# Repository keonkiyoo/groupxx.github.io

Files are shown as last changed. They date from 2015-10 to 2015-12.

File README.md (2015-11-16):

# groupxx.github.io

Team Smart Cane - T06
Group Members: Shadman Shamin, Keon Yoo, Nate Pham, Dusan Micic

Project Description: The development and implementation of a smart cane that read surrounding environment and measures distance between the user and obstacles. The cane is for everybody who uses a cane and geared towards elderly population to help them navigate the streets and pedestrians safely. Based on the threshold safe distance the cane sends a haptic feedback to user to notify/alert the user of nearby obstacles so that they can avoid the obstacles safely.

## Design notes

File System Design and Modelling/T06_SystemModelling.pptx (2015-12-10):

## T06 - Smart Cane System Modelling

Members: Dusan Micic, Shadman Samin, Nathan Pham, Keon Yoo

Document ID: T06_Model_V1
Version : 1.1
Date : 12/9/2015
Location : Git Wiki Page (https://github.com/keonkiyoo/groupxx.github.io/wiki)

## Level - 0 Diagram

3 different Ultrasonic Sensor Inputs

Smart Cane

Power, 9V DC

Haptic Motor Output

Module | Smart Cane
Inputs | The system has three pulse width inputs coming in from 3 Ultrasonic Sensors. Each containing an 8 cycle burst pulses that gives us distance information based on the width of the pulse. Second, we have the 9V DC Power that is connected to the 9V battery that powers the whole system.
Outputs | Digital Output to Haptic Motor for operation
Functionality | Measure the distance between the user and nearby objects. And notifies the user if the object is too close.

## Level 1: Smart Cane

Ultrasonic-1

Ultrasonic-2

Ultrasonic-3

Digital Input/Output

Digital Input/Output

Digital Input/Output

Application Software

SPI Interface Program & Debug

Digital Input/Output

Microprocessor

Digital Output

Haptic Motors

Regulator: 5V

Regulator: 3.3V

9V Battery

## Level - 0: 5V Regulator

Regulator: 5V

Power, 9V DC

5 V (DC)

Module | Regulator: 5V
Inputs | Battery connection with a +9V DC Battery
Outputs | +5V DC Output, Maximum Current: 1A
Functionality | Output a constant 5V DC output from a 9 V

## Level - 0: 3.3V Regulator

Regulator: 3.3V

Power, 9V DC

3.3V (Analog DC)

Module | Regulator: 3.3V
Inputs | Battery connection with a +9V DC Battery
Outputs | +3.3V DC Output, Maximum Current: 1A
Functionality | Output a constant 3.3V output from a 9V

## Level - 0: Ultrasonic Sensor

Ultrasonic Sensor

5V DC, Power

Digital Input/Output

Module | Ultrasonic Sensor
Inputs | 5V DC Input for the Ultrasonic Sensor(From 5V Voltage Regulator)
I/O (Input/Output) Pin | The Microprocessors sends a digital trigger pulse (5V) to the ultrasonic sensor to activate it. The sensor sends back an echo signal by an 8 cycle burst pulse (~5V) on the same pin to the microprocessor. The width of the digital pulse to the microprocessor indicates the obstruction distance. The wider the signal the further the object.
Functionality | Every 100 ms the sensor receive a 10 us trigger to activate it and send back a digital pulse to the microcontroller which contains distance information.

## Level - 0: Microprocessor

Digital Input/Output

Microprocessor

Digital Output (Motors)

5V DC, Power

Module | Microprocessor
Inputs | 5V DC Input for Power (From 5V Regulator) Input 8 burst cycle from the echo of ultrasonic sensor to detect distance.
Outputs | Send output high (~5V) to bias transistor allowing current flow to power motor on when within obstruction distance Output 10us pulse high (~5V) to trigger the Ultrasonic sensors
Functionality | When the microcontroller gets an input from the Ultrasonic sensors it looks at the width of the return pulse to find the distance between the user the object in front. If the distance is less than the safe distance the Digital pins on the outputs go High to notify the user.

## Level - 0: Haptic Motor

Digital Input

3.3V DC, Power

Haptic Motor

Motor Vibration Output

Module | Haptic Motor
Inputs | 3.3V DC Input (from 3.3V Voltage Regulator) Digital Input Connection from Microprocessor (output high ~5 volts)
Outputs | Motor Vibration Output
Functionality | If the Sensors detect an object too close to the user the Microprocessor sends a high bit through one of the digital ports on the microprocessor to turn on the Haptic motors (4.5 – 3.0 Volt required power to operate) to warn the user of an obstruction.

## Smart Cane Flowchart Representation

No

Start

Object Detection

Calculate the distance between Object and Cane

Distance < 30 cm

Yes

Turn on the LED and Haptic Motors to Alert the User

No

Distance < 30 cm

Yes

## State Machine View

Within Motor distance

object detected

No object detected

User Feedback and Operate Motor

Verify Distance

Object Detection

Re-verify distance

Not within motor distance

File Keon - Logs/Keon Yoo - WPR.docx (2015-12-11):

10/11/15 – 10/17/15

Accomplished: Set up the Github page and downloaded desktop GUI for Github. We also narrowed down the design specifications.

10/18/15 – 10/24/15

Accomplished: Met with the team to test Arduino code and the ultrasonic sensors to make sure it was sufficient for the project. We found that the ultrasonic sensor is accurate upwards of 2.5m.

10/25/15 – 10/31/15

Accomplished: Worked on learning how to use the EagleCAD to do the schemaitcs. Worked with Shadman on completing the schematics for the board design.

11/1/2015 – 11/7/2015

Accomplished: Started working on the programming microcontroller. We were having trouble getting the Arduino to program the Atemga 328p on the bread board. One of the students told us to use the AVR dragon to program it and we were able to program the microcontroller.

11/8/2015 – 11/14/2015

Accomplished: Nate and I completed set of code which lighted LED on and off to ensure that microcontroller was working. We set up a sensor for the circuit with a clock pulse which we generated through a code, periodi 100us pulse.

11/15/2015 – 11/21/2015

Accomplished: I found a code online that was used for operating the sensor with the idea of the rising edge pulse and falling edge. However it was beyond our scope of understanding for coding the sensor. We changed the various value within the code that we knew would not result in significant difference in the detection of objects.

11/22/2015 – 11/28/2015

Accomplished: This week we met up as a team to debug and construct our PCB we got from OSH Park. However there were some error on the PCB, it was not matching with the EagleCAD. It was a minor error so we decided it was okay and we ordered correct size parts. However, when we plugged the assembled board to the AVR dragon to program it, it gave us an error saying not enough voltage, so we walked through the circuit and decided to remove the reset LED to give more voltage to the Atmega328p. However, that still did not work. Later in the evening, Shadman told us that it was AVR dragon that was causing the problem and everything was working fine. I soldered the wires that will run through the cane and the board.

11/29/2015 – 12/5/2015

Accomplished: New parts arrived and populated rest of the board. We got together and put together the cane. Nate and I worked on routing the wires through the cane. We had to make some adjustments such as cutting out a hole on the PVC pipe cane to route the wires. Shadman used laser cutter to print out the acrylic case for the board.

12/6/15-12/10/15

Accomplished: We spent this week working on the debugging and optimizing the code. We also worked on the power point presentation and revisions on the HW.

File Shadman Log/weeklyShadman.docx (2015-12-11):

Week 1 | Look for team members, submit resume.
Week 2 | Team formed. Look for parts to be used in the project. Brainstorm project ideas from different project website. Submit Project Proposal.
Week 3 | Built a rough prototype using the sonar sensors. Wrote a small code to interface with the arduino. Meet up with team members to work on the Wiki page
Week 4 | Worked on the product design specification
Week 5 | Worked on the schematic and the design timeline
Week 6 | Accomplishment: The schematic and the board layout is done
Week 7 | Accomplishment: The final boards are waiting to be shipped in. All the parts are ordered
Week 8 | Accomplishment: Final boards are populated with new right order of packages in the LID lab, the boards are tested and can talk to the computer using ISP header. Problems: We discovered the ISP header orientation on the board is not consistent with ISP header on the AVR dragon. Therefore, we spent alot of time trying to debug it.
Week 9 | Accomplishment: Prototype built. PVC cane retrofitted with Three sonar sensors and Laser cut a board to house the board. The vibration motors and all the wires are hidden inside the sensors. Problems: At this stage our prototype is working with three sensors working together to notify the user using haptic feedback.
Week 10 | Accomplishment: Got the prototype working for the final demonstration. Changed the software code to reflect changes. Problems: The sensor does not calculate the distance accurately based on the functional verification testing. Therefore, we changed the code to reflect and react to some arbitrary distance value. The BJT was replaced to reflect a fast switching circuit using a NMOS transistor.

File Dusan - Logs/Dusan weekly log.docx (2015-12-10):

10/11/15 – 10/17/15

Accomplished: Set up the Github page learned how to use it. Got familiar with git bash and git command line in general.

10/18/15 – 10/24/15

Accomplished: Met with the team to test Arduino code and the ultrasonic sensors to make sure it was sufficient for the project. We found that the ultrasonic sensor is accurate upwards of 2.5m.

10/25/15 – 10/31/15

Accomplished: Learned how to use EagleCAD to make the board from the schematic. Designed the board and debugged various issues and DRC errors until it was error free.

11/1/2015 – 11/7/2015

Accomplished: Downloaded Atmel studio to help with programing the microcontroller. The group got together to do initial tests on the range sensors and we made sure the frequency of the resonator we were using was sufficient.

11/8/2015 – 11/14/2015

Accomplished: We ordered the necessary parts for the board and sent the board off to get manufactured.

11/15/2015 – 11/21/2015

Accomplished: We received the parts and were still waiting for the boards to be manufactured.

11/22/2015 – 11/28/2015

Accomplished: We received the PCB’s from the manufacturer and began to learn how to apply solder paste, place components and baked in the oven. Shadman and I got together and populated two boards initially. We discovered that some of the parts were of the wrong size and we ordered new ones to correct for this. Other than the resonator (which was to small for its pads), everything on the board worked fine.

11/29/15 – 12/5/15

Accomplished: The new parts arrived and the whole group got together and populated the other two boards. All components fit perfectly. We built the cane prototype using PVC pipe.

12/6/15 – 12/10/15

Accomplished: This week we spent most of the time debugging various problems with the prototype and fine tuning the code. Next we got to work on the presentation and the various documentation that needs to be turned in.

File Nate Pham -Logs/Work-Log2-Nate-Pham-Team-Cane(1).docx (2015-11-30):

11/1/2015 – 11/7/2015

Accomplished: This week no battery indicator circuit was implemented. At the start of this week, Keon and I started working to get the microcontroller to be programmed on the breadboard itself and we were getting used to the software to operate the arduino and program the microcontroller and how to program the microcontroller on the board with various connections. We spend much of the time figuring out how to program the microcontroller on the arduino after researching through various websites we were unable to find anything that was usable through the information. A fellow student helped us though. He let us know that we should be using the AVR dragon with Atmel studio to program the chip on the arduino. We went to program the chip and were able to get the chip removed from the circuit and place it on the breadboard to ensure the effectiveness of the programming which ended up working well.

11/8/2015 – 11/14/2015

Accomplished: The time spent this week was recreating the circuit of the Arduino Nano on the breadboard with an external oscillator and connections to set pins. I set up the replicated circuit on the breadboard and began testing for the functionality of the microcontroller. Keon and I completed a set of code which set an output of the chip to blink on and off for and LED to ensure that it was working correctly. It ended up working well but with less output voltage than expected. We messed around with different coding structures for running the microcontroller and found various codes online that we tested but were fairly incomplete for the complete circuitry. We set up a sensor for the circuit with a clock pulse which we generated through a code which was a periodic 100us pulse. The result of the sensor though was a constant distance detection. We realized how the sensor operates but measuring the rising edge of the sent back signal to the falling edge of the signal and that is how it signifies the distance of the obstruction or object. I started tweaking with some characteristics of the clock pulse but only further realized that a constant clock pulse will not work for the circuitry.

11/15/2015 – 11/21/2015

Accomplished: Keon found a code online that was used for operating the sensor with the idea of the rising edge pulse and falling edge in consideration and it was beyond our scope of understanding for coding the sensors. We changed various values within the coding which we know that we could change without much difference to the detection of objects but we made sure the sensors still worked when changing up the code.

I ended up testing the circuit. I found that the result was when I set the motor to vibrate within 5 centimeters that the sensor would detect within that range but going from ~10cm – 15cm that there would be some detection of some obstruction though the sensor shouldn’t consider such a distance since it is beyond its notifying parameter. This was a consistent issue. I tried changing the ranges of detection and even with various values it kept on a having a repetitive result. I decided to pass off the results to Shadman for he wanted to test some things with the circuit.

11/22/2015 – 11/28/2015

Accomplished: This week we met up as a team to work on the board debug and construction. The boards were received from the EPL lab and Shadman and Keon did some of the soldering of the basic circuitry. We realized that when the boards were sent in that it was actually an incorrect schematic rather than the newest and updated one. Shadman was reviewing why an LED was as bright as the other LEDs and as a group we confirmed that it was okay.

We went over why there was only ~1.7 volts dropped from the reset switch to ground. It wasn’t a big deal until we got help from another student which he said that there needs to be a more significant voltage felt on the reset connection to program the chip. I noticed that the path to ground after the pull up resistor had a 220 ohm resistor and a LED on another path to ground which was in parallel with the reset switch. It became obvious that the path wasn’t dropping a significant voltage. The group suggested putting on a 10k ohm resistor before the LED to ensure that the voltage drop was >2.5 volts since the LED will drop .7 volts and the two 10k resistors are in a voltage divider configuration. The remeasured voltage to group was ~3 volts which was good for programming the chip.

Shadman and I then set up the chip to be programmed through the ISP pins to the AVR dragon and we weren’t able to get it to detect the voltage of the chip meaning that there was an error somewhere in the configuration. Shadman realized that one of the pins was incorrectly connected to the AVR dragon since each pin was wired with individual wires with male connectors separately in the AVR dragon input. Once that was adjusted, we received another error. I suggested to change the AVR dragon since I knew the AVR dragon and Atmel studio were fairly inconsistent in their operation. Once the AVR dragon was switched, we were able to program the chip from on the board and we set an external oscillator setting on the chip. After this programming, we received a 16.00MHz signal coming off of the external oscillator configuration. Everything works well. The next test is to retrieve an input and output a motor activation.

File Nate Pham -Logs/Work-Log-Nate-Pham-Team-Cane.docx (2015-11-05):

10/11/15 – 10/17/15

Accomplished: We set up the Github page and our own personal accounts for this week. We also put in the desired specifications for which we decided our narrowed down project. As a team, the obstruction notifying cane for the disabled was indicated as the best project and with a good difficulty. We sent in our request to the instructor.

10/18/15 – 10/24/15

Accomplished: Met up with team and proceeded to test Arduino code with Shadman and ensure the sufficiency of the ultrasonic sensors used in accessory to the Arduino board. The test came out sufficient with the accuracy of the sensor being at a suitable (realistic) value when testing. We were precise in our distance that tested upwards of 2.5 meters. Note: We had to make some changes to the code due to some approximation errors occurring on the Arduino output code. A slight implementation of an AND statement fixed the correction.

We also went over the CAD design of the product and what other things the product may need as well.

The team through this week worked on the product design specifications sheet and tried to make sure it covered the necessary areas.

10/25/15 – 10/31/15

Accomplished: This week I studied various circuits for giving signs of a low battery indication, of the circuit, for it is important for a disabled person. I looked at at least a few and narrowed it down to a couple of selections. Also, after the team meeting, I went and tested the cell phone battery vibrator motors to test if they are sufficient, and when the precise current is running through the motors the vibration is sufficient; otherwise, with low current, the doesn’t have much of a vibration and may not have a good vibration feel on the handle of the device. We will have to study a good output for running the vibrating motors.

As a team, we set up the needed schedule for the team to navigate our progress with and what needs to be done with what people. The Schematic also is being completed by Keon and Shadman while Dusan and I will look through it for validity.

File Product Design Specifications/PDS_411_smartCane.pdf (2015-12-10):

Portland State University

Product Specification Document (PDS)

Smart Cane

Authors:

Shadman Samin

Keonki Yoo

Nathan Pham

Dusan Micic

Supervisor:
MARK FAUST
ANDREW GREENBERG

December 10, 2015

## Contents

1 Introduction | 2
2 Requirements | 2
3 Appendix | 4

1

## 1 Introduction

### 1.1 Project Overview

In order to successfully alert the users of nearby objects through a sensor and use a haptic feedback system of LEDs’ and Vibration motors to notify the people around and the user.
The purpose of this project requirement is to provide the technical specification to the contractors who will design, manufacture and test the devices. The user for these devices will be medical and daily cane users.

### 1.2 Definitions, Acronyms and Abbreviations

- Haptic - Sense of touch. We will use a vibration sensor to physically alert the user.
- Sensor - Ultrasonic Sensor that measures distance.
- Buyer - Third party consumer that will buy the product from stores for personal use.
- Device,Produce,Item - The smart Walking cane

### 1.3 Communication

The product engineering team can be contacted using the following information: Email: shadman@pdx.edu, Phone: 9177448589

### 1.4 Location of Document

The document along with the history of product repository can be located in the following location:
https://github.com/keonkiyoo/groupxx.github.io/wiki/Homework

### 1.5 Target Audience

This document is intended for buyers, manufacturers, Professor Mark Faust, Professor Andrew Greenberg, Teaching Assistants and project team to agree on requirements for design and production of ’The Smart Cane’.

## 2 Requirements

This section the requirements for the design process under different criterion and methodology.

2

### 2.1 General Requirements

The general requirements includes engineering design, manufacture, test and delivery of final system to the buyer.
Externally imposed Constraints:
- PCB must have 2 layers.
- PCB must have no linear dimension < 2 cm or > 30 cm
- PCB must have more than 25% surface mount components

Operational:

– he cane must have an accurate range of detection of an obstruction within +- 3 cm of indicated distance which is 30cm.

– The power source of the device must last a minimum of six hours before needing to be replaced meaning the number of batteries needed will depend on power consumption during testing. (Ideally a long time due to it being a walking device)

– The device may be water resistant due to the nature of the environment (walking outside)

– All components must be properly secured to the cane to avoid breaking in the event of the cane hitting an object.

– The sensors should be able to record and compute at least 10 sample per second, i.e. The sampling frequency of the range detecting sensor must be at least 10 Hz.
– Cane may not exceed more than 5 pounds in weight.

Environmental:

– The device may be water resistant due to the nature of the environment (walking outside)

– All components must be properly secured to the cane to avoid breaking in the event of the cane hitting an object.

Technical Support:

– The vendor shall support technical support for upto 1 year within the purchase date of the product.

– The vendor shall support device warranty upto 1 year.
– The latest hardware/software should supported in the manufactured hardware/product.

Budget:

– The cost of the device must be no more $100 than in order to be affordable.

3

Legal:

– The device may comply with US Patent and Copyright Law.

– The device may pass FDA approval as medical device.

### 2.2 Specific Feature and Function

– A notification should be given to the user via a vibrating motor when an obstruction is detected.

– No extra steps should be needed after turning the Walking Cane on.

– Each device should be fully functional without the need of extra hardware.

– The device should have an ON-OFF switch

– The device must be self-operated, e.g. no additional computer or any kind of computerized system will be required for its operation.

### 2.3 Required Documents

– One set of user’s operation and maintenance manual

– The schematic diagrams.

– The datasheet of main components

– List of recommended spare parts if any.

– Test documents

## 3 Appendix

The addition, change from previous version. Changes in the PDS is recorded below in a table.

4

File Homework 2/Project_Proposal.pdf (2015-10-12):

# Project Proposal Smart Walking Cane

Shadman Samin, Keon Yoo, Nate Pham, Dusan Micic

October 12, 2015

## 1 Objective

To build a smart walking cane that can work simultaneously as a traditional walking stick, as a smart alert system and a diagnostic tool for doctors. As the next generation of devices are becoming more intelligent, the idea of this project is to embed intelligence into traditional devices. Alot of daily users of walking canes will be reluctant to use smart tags/wearables but many are fond of the traditional walking canes. So the market is still lacking smart walking canes for daily users and specialized biomedical use.

## 2 Description of Operation

The idea of this project is to incorporate embedded chips into a walking canes and add sensors to it get real time data on walking patterns, also the cane can work as an alert system to help users dodge obstacles infront of them. Two Sonar sensors will be attached infront to help guide the user to avoid obstacles to LED and a small sound sensor to buzz the user. Also, the walking cane will come with a gyroscope and accelerometers, this will help Doctors diagnose and analyse walking patterns by looking at data for longer time periods to help understand if the patients walking patterns is improving or not. The system will come with a network module attached that will talk to a HUB computer over a 2.4 GHz network bandwidth the relay data in real time. Also, the system will come with a SD card module attached to record data for longer time periods.

## 3 Compliance to Project Requirement

The project ’Smart Cane’ was determined to meet all requirements for the hardware, design, parts availability and timeline. The most challenging part of this project would be the implementation and board design. Our team is skilled in different areas of the project from firmware design, to analog, and the post processing of the data in Matlab for visual display of the data. Throughout the project the team wiki site will be updated for each iteration and progress throughout the project. The team already owns an inventory of sensors and network modules from previous projects that can be incorporated into this projects, so the budget for this projects is aimed to be minimal. Block diagram, schematics, programming code, datasheets and other useful matertials will be available in the teams wiki page.

1

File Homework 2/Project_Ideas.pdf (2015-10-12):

# Project Ideas

Shadman Samin, Keon Yoo, Nate Pham, Dusan Micic

October 12, 2015

## 1 Rough Ideas

The team came up with few ideas at the beginning before finalizing the top four projects of the projects below.

- Environment Sensing Quadcopter
- Brightness Changing Lantern
- Equalizer/Mixer Board for Music
- Mail Notifier
- Home Automation
- Portable Heating Element
- Smart Cane

## 2 Final Ideas:

### 2.1 Brightness Changing Lantern

The brightness changing lantern is a device that has the ability to change its level of brightness due to the intensity of darkness on the outside. The device would use a microprocessor to has a variable adjusting brightness which allows the user to conserve battery if needed. Two sensors would be at the top to detect brightness while using leds for the light.

### 2.2 Equalizer/Mixer Board

The board is an enhancement tool such as a guitar pedal going into an amplifier. This board will allow the user to increase various ranged such as the 10 Hz to 100 Hz range of frequency or the 500 Hz to 1000 Hz if needed for special utilization for a specific sound effect. Also, if the user would like to decrease the effect, the user could do that as well.

### 2.3 Portable heating element

The portable heating element is a on the go user friendly device. This can be used for a cup the size of a mug or a taller mug with a fluid near the top. With a two pressure sensor safety, the device is placed on a cup and increases the fluid to a desired temperature. The safety keeps the device from being on without it being on the edge of a cup.

### 2.4 Smart Walking Cane

The smart cane is a biomedical device that will work as a tool for biomedical diagnosis to learn walking pattern and behaviors of its users to help diagnose disabilities and disorders. This board will have smart capabilities of sensing nearby objects to alert the user and have embedded accelerometers and gyroscopes connected to a network module to study walking patterns from a remote hub. We will then understand walking patterns using variable statistical signal processing.

1

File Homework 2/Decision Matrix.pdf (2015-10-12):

Decision Matrix

The decision matrix is based on AHP methodology and the team made the decision based on the total weight, and the top choice was picked. Analytical Hierarchy Process (AHP) method is used to come up with the best project. First, the criterion is compared with each other to get a fair ratio and weight. Then comparative analysis is performed between the projects to find the best results.

Numerical values used for comparative analysis between each criteria:
- | 1 | – | equal
- | 3 | – | “moderately” more important
- | 5 | – | “strongly” | more important
- | 7 | –” | very | strongly” | more important
- | 9 | – | “extremely” | more important
| Requirem ent | Abili ty | Co st | Safe ty | Invento ry | Original ity | Challengi ng | Tim e | Mea n | Weig ht
Requirem ent | 1 | 1 | 1 | 3 | 3 | 3 | 3 | 3 | 1.98 | 0.22
Ability | 1 | 1 | 3 | 3 | 3 | 3 | 1 | 1 | 1.73 | 0.19
Cost | 1 | 1/3 | 1 | 1/3 | 1 | 1/5 | 1/3 | 1/3 | 0.45 | 0.05
Safety | 1/3 | 1/3 | 3 | 1 | 3 | 3 | 3 | 3 | 1.51 | 0.16
Inventory | 1/3 | 1/3 | 1 | 1/3 | 1 | 1/3 | 1/3 | 1/5 | 0.41 | 0.04
Originality | 1/3 | 1/3 | 5 | 1/3 | 3 | 1 | 1/3 | 1/5 | 0.66 | 0.07
Challengi ng | 1/3 | 1 | 3 | 1/3 | 3 | 3 | 1 | 1/3 | 1 | 0.11
Time | 1/3 | 1 | 3 | 1/3 | 5 | 5 | 3 | 1 | 1.49 | 0.16
| | | | | | | | | 9.23 | 1

Table 1: Analytical Hierarchy Process (AHP) to find the weights for each criterion

Project: | Brightness Changing Lantern | Equalizer Mixer Board | Portable Heating Element | Smart Cane
Criteria | Weight
Meets the requirement | 9 | 5 | 5 | 8 | 9
Technical Ability to Develop | 7 | 7 | 6 | 6 | 7
Estimated Cost ( 1 - Most, 2 -Least) | 2 | 2 | 1 | 1 | 2
Safety | 6 | 6 | 6 | 3 | 6
Parts in Inventory ( least to most available) | 2 | 2 | 2 | 1 | 2
Originality | 4 | 2 | 2 | 4 | 4
Challenging | 4 | 2 | 4 | 4 | 4
Time to production ( 1 most, 6 least) | 6 | 6 | 3 | 4 | 4
Total | 40 | 32 | 29 | 31 | 38

Table 2: Showing the weighted results for different project under AHP methodology

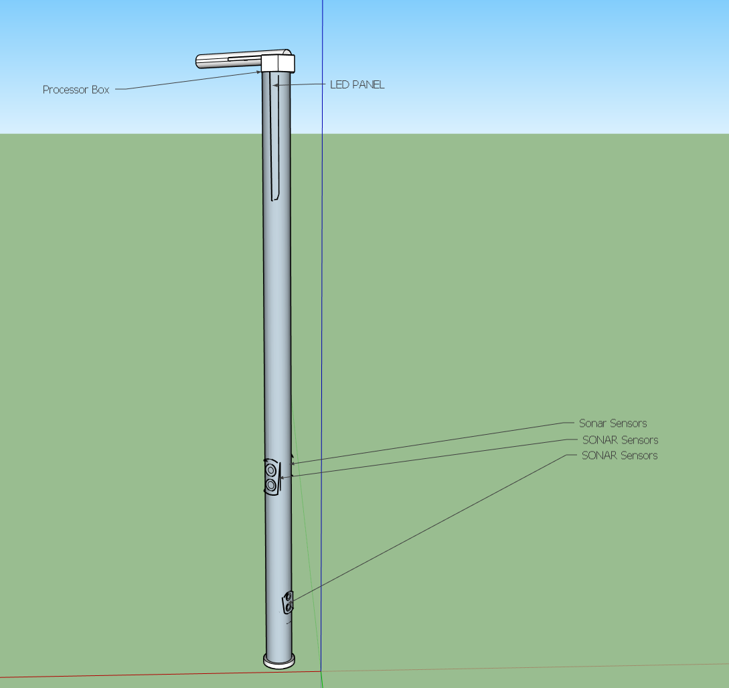
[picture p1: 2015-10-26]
3D CAD Design/3D CAD Design.PNG

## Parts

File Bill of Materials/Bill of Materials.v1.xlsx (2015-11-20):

Designators | Description |  | Value | Device | Package | Part# | Manufacturer | Mount Type | Unit Price | Quantity | Total Price | Status | Payment
Capacitor - 10uF | CAPACITOR | American symbol | 10uF | C-USC0805K | C0805K | GRT21BR60J106ME01L | Murarta Eelectronics North America | Surface Mount | 0.0499 | 100 | 4.99 | Received | Shadman
Capacitor - 100nF(0.1uF) | CAPACITOR | European symbol | 100nF | C0805K | C0805K | CL21F104ZBCNNNC (http://www.digikey.com/product-detail/en/GRM216R71H103KA01D/490-1664-1-ND/587472) | Samsung Electro-Mechanics America, Inc. (http://digikey.com/Suppliers/us/samsung-electro-mechanics.page?lang=en) | Surface Mount | 0.022 | 30 | 0.66 | Received | Shadman
CSTCE16M0V53-R0 | Ceramic oscillator with built in capacitors such as ZTT-12MHz |  | 16M | CERMOSCILL-THM | CERM_OSC | CSTCE16M0V53-R0 | Murarta Eelectronics North America | Surface Mount | 0.4 | 10 | 4 | Received | Shadman
 | LED Green |  | Green |  |  | LTST-C171GKT | Lite-On Inc. | Surface Mount | 0.2 | 20 | 4 | Received | Shadman
LEDs | LED Orange |  | Orange |  |  | LTST-C170KFKT (http://optoelectronics.liteon.com/upload/download/DS-22-99-0185/S_110_LTST-C170KFKT.pdf) | Lite-On Inc. | Surface Mount | 0.213 | 10 | 2.13 | Received | Shadman
Power Regulator +5 | 800mA and 1A Low Dropout (LDO) Positive Regulator |  | REG1117 | REG1117 | SOT223 | NCP1117DT50RKGOSCT-ND | On Semiconductor | Surface Mount | 0.392 | 10 | 3.92 | Received | Shadman
Power Regulator +3 | 800mA and 1A Low Dropout (LDO) Positive Regulator |  | REG1117 | REG1117 | SOT223 | NCP1117DT33T5GOSCT-ND | On Semiconductor | Surface Mount | 0.392 | 10 | 3.92 | Received | Shadman
Resistor - 1M ohm | RESISTOR | European symbol | 1M | RR0603 | R0603 | RC0603FR-071ML | Yageo | Surface Mount | 0.01 | 40 | 0.4 | Received | Shadman
Resistor - 10k ohm | RESISTOR | European symbol | 10K | RR0603 | R0603 | RC0603JR-0710KL | Yageo | Surface Mount | 0.008 | 40 | 0.32 | Received | Shadman
Resistor - 510 ohm | RESISTOR | European symbol | 510 | RR0603 | R0603 | RC0603JR-07510RL | Yageo | Surface Mount | 0.008 | 40 | 0.32 | Received | Shadman
Resistor - 100 ohm | RESISTOR | European symbol | 100 | RR0603 | R0603 | RC0603FR-07100RL | Yageo | Surface Mount | 0.008 | 40 | 0.32 | Received | Shadman
Resistor - 220 ohm | RESISTOR | European symbol | 220 | RR0603 | R0603 | RC0603JR-07220RL | Yageo | Surface Mount | 0.01 | 40 | 0.4 | Received | Shadman
Tactile swtich | Tactile Switch 4 Pins | SPST NO | TACTILE-SWITCH-PTH | TACTILE-SWITCH-PTH | TAC-SWITCH-PTH |  |  | Surface Mount | 0.256 | 10 | 2.56 | Received | Shadman
 |  |  |  |  |  |  |  |  |  |  | 0 | Shipped | Shadman
ATMEGA328P | Microprocessor |  |  |  |  | ATMEGA328P |  | DIP | 3.7 | 5 | 18.5 | Received | Shadman
Wire Pre-Crimped | Jumper Cables |  |  |  |  | 4 Pin Female - Female |  |  |  | 50 | 9.95 | Shipped | Shadman
Solid Wire Kit | Cables |  |  |  |  | Cables |  |  |  | 1 | 22 | Received | Shadman
 |  |  |  |  |  |  |  |  |  |  |  | Shipped
Digikey |  |  | Shipping |  |  |  |  |  |  |  | 11.38 | Received | Shadman
Polulu |  |  | Shipping |  |  |  |  |  |  |  | 4.45 | Received | Shadman
OSH Park Board
 | Board OSH Park |  |  |  |  |  |  |  |  | 3 | 36.8 | Shipped | Shadman
 |  |  |  |  |  |  |  |  |  | Total | 131.02

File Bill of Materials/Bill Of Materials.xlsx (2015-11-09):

Description | Part No# | Package | Mount Type | Size | Quantity | Unit Price | Total Price | Inventory
Power Regulator +5 | NCP1117DT50RKGOSTR-ND | SOT223 | Surface Mount | - | 10 | 0.15686 | 1.5686 | Yet to Order
Power Regulator +3 | NCP1117DT33T5GOSTR-ND | SOT224 | Surface Mount | - | 10 | 0.15686 | 1.5686 | Yet to Order
Resistor - 1M Ohm |  |  |  |  | 10 |  | 0
Resistor - 10K Ohm |  | 9803002 |  |  | 10 |  | 0
Resistor - 500 Ohm |  |  |  |  | 10 |  | 0
Resistor - 220 Ohm |  |  |  |  | 30 |  | 0
Resistor - 100 Ohm |  | 9dgi9fgidfg |  |  | 10 |  | 0
 |  |  |  |  |  |  | 0
 |  |  |  |  |  |  | 0
 |  |  |  |  |  |  | 0
 |  |  |  |  |  |  | 0
 |  |  |  |  |  |  | 0
 |  |  |  |  |  |  | 0
 |  |  |  |  |  |  | 0
 |  |  |  |  |  |  | 0
 |  |  |  |  |  |  | 0
 |  |  |  |  |  |  | 0
 |  |  |  |  |  |  | 0
 |  |  |  |  |  |  | 0
 |  |  |  |  |  |  | 0
 |  |  |  |  |  |  | 0
 |  |  |  |  |  |  | 0
 |  |  |  |  |  |  | 0
 |  |  |  |  |  |  | 0
 |  |  |  |  |  |  | 0
 |  |  |  |  |  |  | 0
 |  |  |  |  |  |  | 0

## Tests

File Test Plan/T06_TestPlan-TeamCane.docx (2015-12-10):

# “Vibrating Walking Cane”

TEST PLAN

Document: TEST_PLAN_w_Cane.pdf

Date of Test: / /

Approval Date: _________________

Approver: _________________

Version Date:

Version Date Author

1.9.310 11/24/2015 Keon, Nathan, Shadman, Dusan

Vibrating Walking Cane: System Test Plan

Introduction Documentation & Reference to Design Specs: Page 1

Table of Contents: Page 2

List of Tests and Test Plan: Page 3

Sensor Integration Test: Page 4

Voltage & Frequency Parameter Test: Page 5

Functional Cane Accuracy Test: Pages 6 - 7

Power Supply Parametric Test: Page 8

Environmental Perspiration Test: Page 9

Cane Drop Environmental Stress Test: Page 10

Test Plan:

Materials and equipment Required:

- Walking Cane Detector
- 9V Battery
- Oscilloscope (for parametric testing)
- Spray bottle
- Multi-meter

Module Test

- Power
- Battery Life

Integration Test

- Interaction between Ultrasonic Sensors and Microcontroller
- Microcontroller to Vibration motor

Parametric Test

- Output voltage High Testing
- Output voltage Low Testing
- Number of Detections per Second

Functional Test

- Accuracy of Sensor within +/- 3 cm detector accuracy

Environmental Test:

- Water Resistant
- Humidity Test
- Drop Test

Note:

This Test plan includes a product design specifications document which indicates the requirements which are stressed of importance and tested through the test plan. All the system requirements and system design are accessible at: https://github.com/keonkiyoo/groupxx.github.io

Test Case Name: | Sensor Integration Test | | | Test ID# | IT-1
Description: | Verify each sensor is detecting correctly and the microcontroller is sending a signal to power the motor vibrator output. | | | Type: | White Box
| | | | | Black Box X

Tester Information:
Name of Tester: | | | | Date:
Hardware Version: | 1.0 | | | Time:
Test Setup | The Cane will receive an input from the three sensors and cause a motor vibration when the ultra-sensor sends a signal and detects an obstruction within the close proximity of 30 cms.
Step: | Action | Expected Result | Pass | Fail | N/A | Comments
1 | Place left sensor within the set sensor range | Vibration
2 | Place middle sensor within the set sensor range | Vibration
3 | Place right sensor within the set sensor range | Vibration

Test Case Name: | Voltage & Frequency Parameter Test | | | Test ID# | PT-1
Description: | Test the Output Voltage High and Low, and verify (Number of Detections per second) | | | Type: | White Box X
| | | | | Black Box

Tester Information:
Name of Tester: | | | | Date:
Hardware Version: | 1.0 | | | Time:
Test Condition | T = 25 degrees Celsius
Test Setup | The cane will receive output signal every 100 ms with a variable pulse width based on distance. Use an oscilloscope probe and measure the output at the digital pin (ECHO) on the board.
Step: | Action | Expected Result | Pass | Fail | N/A | Comments
1 | Use the oscilloscope to measure the output signal from the microprocessor to the ultrasonic sensors | Square Wave with peak to peak voltage of 3 - 5 volts
2 | Use the oscilloscope to measure the number of detections per second from the echo pin of the sensors | Detect a minimum 10 cycles per second square wave

Test Case Name: | Functional Cane Test | | | Test ID# | FT-1
Description: | Checks to ensure accuracy of the ultrasonic sensors within +/- 3 cms of the set sensor range. | | | Type: | White Box
| | | | | Black Box X

Tester Information:
Name of Tester: | | | | Date:
Hardware Version: | 1.0 | | | Time:
Test Setup | Device should be properly working before performing this test. First, move the ultrasonic sensor to just before the motor vibrates. Second, at the distance once the motor begins vibrating, mark the distance from the wall to the sensor and record the data. Thirdly, move the cane away from the wall until the motor stops vibrating and mark the distance. Lastly, ensure accuracy of the detector by comparing data to motor vibration range.
Step: | Action | Expected Result | Pass | Fail | N/A | Comments
1 | Program the Microcontroller and set indicated range for motor vibration | Program should be tested to make sure the sensor is sending signals to the motor at a frequency of 10 detections per second. The User sets the sensor range at which the motor vibrates
2 | Perform Accuracy test moving toward obstruction | Move the cane slowly towards a wall and mark the indicated range at which the motor vibrates, accuracy should be +/- 3cms
3 | Perform Accuracy test moving away from obstruction | Move the cane slowly away from the wall until the motor stops vibrating and mark the distance. The accuracy should be +/- 3cms.
4 | Calibrate | Compare the information from the distance moving toward the wall and away from the wall and ensure each is within +/- 3 cms of the set sensor range. If out of range, set sensor range to even out the distances.
5 | Repeat steps 2, 3 and 4 if needed | Device should accurately activate at set distance and vibrate the motors(+/- 3cms of accuracy of obstruction)

Test Case Name: | Power Supply Module (Parametric Test) | | | Test ID# | PT-2
Description: | Verify the power supply voltage and the current levels on the board while turned on, and verify how long the battery will last while operating. | | | Type: | White Box
| | | | | Black Box X

Tester Information:
Name of Tester: | | | | Date:
Hardware Version: | 1.0 | | | Time:
Test Condition | T = 0 degrees, Input Voltage 9V, current = approximately 220mA
Test Setup | Connect the battery to the multi-meter while the board is on and measure the current and voltage output. Leave the cane ON until there is no current flowing out of the battery looking at the multi-meter.
Step: | Action | Expected Result | Pass | Fail | N/A | Comments
1 | Turn on the switch | 9V and current at approximately 220mA
2 | Turn off the switch | No output
3 | Turn on the switch and leave it ON until it runs out. | Current must be outputting from the battery for at least 4 hours

Test Case Name: | Environmental Perspiration Test | | | Test ID# | ET-1
Description: | Ensure product is usable in a high humidity environment or the rain of the outdoors. | | | Type: | White Box
| | | | | Black Box X

Tester Information:
Name of Tester: | | | | Date:
Hardware Version: | 1.0 | | | Time:
Test Condition | T = 0 - 25 degrees celsius, High humidity environment
Test Setup | The cane is to be fully built and functional before performing this test. A spray bottle or rainy day is to be present.
Step: | Action | Expected Result | Pass | Fail | N/A | Comments
1 | Use the spray bottle and spray each of the sensors several times | The sensors should still accurately detect and vibrate when in sensor range.
2 | Allow the cane in rainy weather for 30 minutes | Upon retesting, the cane should ensure no shorts or electrical errors by performing an functional accuracy test

Test Case Name: | Cane Drop Test (Environmental Test) | | | Test ID# | ET-2
Description: | Performing a durability test by dropping the cane from various heights | | | Type: | White Box
| | | | | Black Box X

Tester Information:
Name of Tester: | | | | Date:
Hardware Version: | 1.0 | | | Time:
Test Setup | The cane is to be fully built and functional before performing this test. A repeated drop from the cane being vertical and a drop from a height horizontally is to be performed.
Step: | Action | Expected Result | Pass | Fail | N/A | Comments
1 | With the cane in an upright position tile with the bottom on the floor, allow the cane to drop naturally from the top position 3 times (onto concrete or tile) | The cane will be fully functional and vibrate when in the motor activation range
2 | Drop the cane horizontally from 5 feet up from the floor (onto concrete or tile) | The cane will be fully functional and vibrate when in the motor activation range

Version: 1.9.310 Date: 11/24/2015

Project Test Plan Page 2

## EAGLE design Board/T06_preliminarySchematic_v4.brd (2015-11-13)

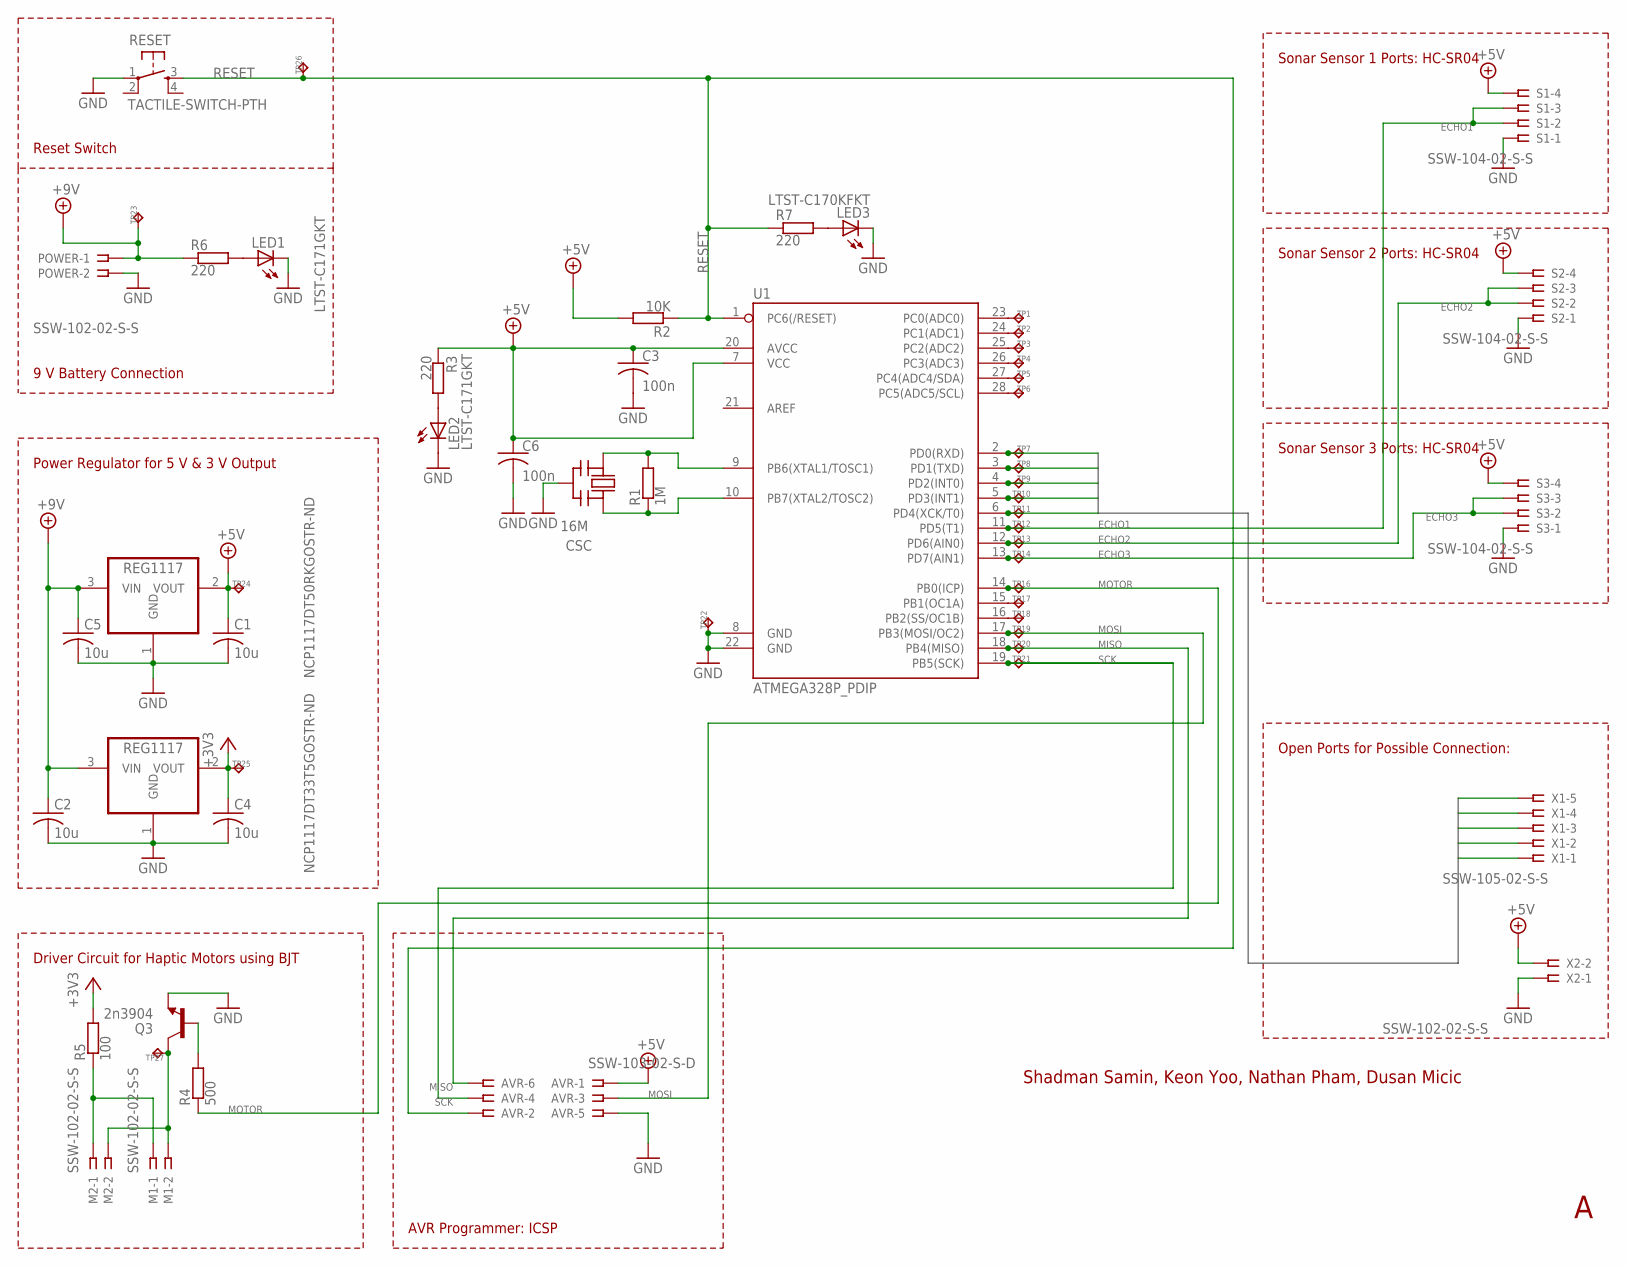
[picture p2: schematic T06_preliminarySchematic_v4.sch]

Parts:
AVR: SSW-103-02-S-D
C1, C2, C4, C5: 10u; C0805K
C3, C6: 100n; C0805K
CSC: 16M; CSTCR-G
LED1: LTST-C171GKT; CHIPLED_0805
LED2: LTST-C171GKT; CHIP-LED0805
LED3: LTST-C170KFKT; CHIP-LED0805
M1, M2: SSW-102-02-S-S
NCP1117DT33T5GOSTR-ND, NCP1117DT50RKGOSTR-ND: REG1117; SOT223
POWER: SSW-102-02-S-S
Q3: 2n3904; TO-92
R1: 1M; R0603
R2: 10K; R0603
R3, R6, R7: 220; R0603
R4: 500; R0603
R5: 100; R0603
RESET: TACTILE-SWITCH-PTH; TAC-SWITCH-PTH
S1, S2, S3: SSW-104-02-S-S
TP1, TP2, TP3, TP4, TP5, TP6, TP7, TP8, TP9, TP10, TP11, TP12, TP13, TP14, TP16, TP17, TP18, TP19, TP20, TP21, TP22, TP23, TP24, TP25, TP26, TP27: TPPAD1-13; P1-13
U1: ATMEGA328P_PDIP; DIL28-3
X1: SSW-105-02-S-S
X2: SSW-102-02-S-S

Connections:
+3V3: C4.1, NCP1117DT33T5GOSTR-ND.2 (VOUT), R5.2, TP25.TP
+5V: AVR.1, C1.1, C3.1, C6.1, NCP1117DT50RKGOSTR-ND.2 (VOUT), R2.2, R3.1, S1.4, S2.4, S3.4, TP24.TP, U1.7 (VCC), U1.20 (AVCC), X2.2
+9V: C2.1, C5.1, NCP1117DT33T5GOSTR-ND.3 (VIN), NCP1117DT50RKGOSTR-ND.3 (VIN), POWER.1, R6.1, TP23.TP
BU0: TP7.TP, U1.2 (PD0(RXD)), X1.1
BU1: TP8.TP, U1.3 (PD1(TXD)), X1.2
BU2: TP9.TP, U1.4 (PD2(INT0)), X1.3
BU3: TP10.TP, U1.5 (PD3(INT1)), X1.4
BU4: TP11.TP, U1.6 (PD4(XCK/T0)), X1.5
D16: TP18.TP, U1.16 (PB2(SS/OC1B))
ECHO1: S1.2, S1.3, TP12.TP, U1.11 (PD5(T1))
ECHO2: S2.2, S2.3, TP13.TP, U1.12 (PD6(AIN0))
ECHO3: S3.2, S3.3, TP14.TP, U1.13 (PD7(AIN1))
GND: AVR.5, C1.2, C2.2, C3.2, C4.2, C5.2, C6.2, CSC.2 (GND), LED1.C, LED2.C, LED3.C, NCP1117DT33T5GOSTR-ND.1 (GND), NCP1117DT50RKGOSTR-ND.1 (GND), POWER.2, Q3.1 (E), RESET.1, S1.1, S2.1, S3.1, TP22.TP, U1.8 (GND), U1.22 (GND), X2.1
MISO: AVR.6, TP20.TP, U1.18 (PB4(MISO))
MOSI: AVR.3, TP19.TP, U1.17 (PB3(MOSI/OC2))
MOTOR: R4.1, TP16.TP, U1.14 (PB0(ICP))
unnamed: CSC.3 (OUT), R1.1, U1.10 (PB7(XTAL2/TOSC2))
unnamed: CSC.1 (IN), R1.2, U1.9 (PB6(XTAL1/TOSC1))
unnamed: TP1.TP, U1.23 (PC0(ADC0))
unnamed: TP2.TP, U1.24 (PC1(ADC1))
unnamed: M1.1, M2.1, R5.1
unnamed: TP3.TP, U1.25 (PC2(ADC2))
unnamed: LED1.A, R6.2
unnamed: LED2.A, R3.2
unnamed: LED3.A, R7.2
unnamed: Q3.2 (B), R4.2
unnamed: M1.2, M2.2, Q3.3 (C), TP27.TP
unnamed: TP4.TP, U1.26 (PC3(ADC3))
unnamed: TP5.TP, U1.27 (PC4(ADC4/SDA))
unnamed: TP6.TP, U1.28 (PC5(ADC5/SCL))
unnamed: TP17.TP, U1.15 (PB1(OC1A))
RESET: AVR.2, R2.1, R7.1, RESET.3, TP26.TP, U1.1 (PC6(/RESET))
SCK: AVR.4, TP21.TP, U1.19 (PB5(SCK))

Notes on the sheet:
9 V Battery Connection
Driver Circuit for Haptic Motors using BJT
Sonar Sensor 3 Ports: HC-SR04
Sonar Sensor 2 Ports: HC-SR04
Sonar Sensor 1 Ports: HC-SR04
Shadman Samin, Keon Yoo, Nathan Pham, Dusan Micic
Reset Switch
Power Regulator for 5 V & 3 V Output
AVR Programmer: ICSP
Open Ports for Possible Connection:

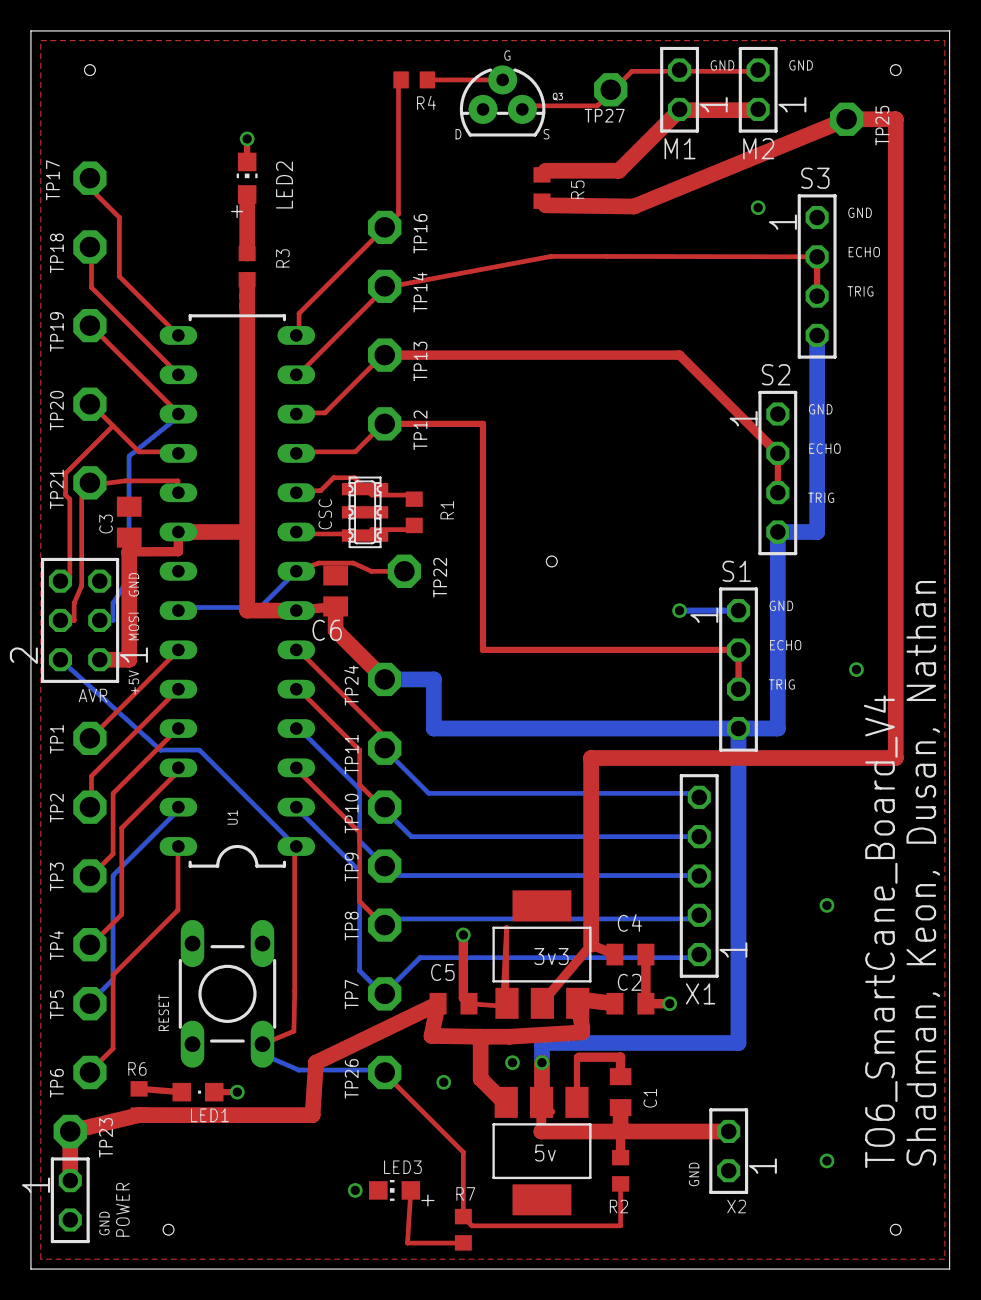
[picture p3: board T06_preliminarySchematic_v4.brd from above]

Board: 2 copper layers, 59.4 x 80.0 mm, 57 parts (0 on the bottom side), 33 nets.

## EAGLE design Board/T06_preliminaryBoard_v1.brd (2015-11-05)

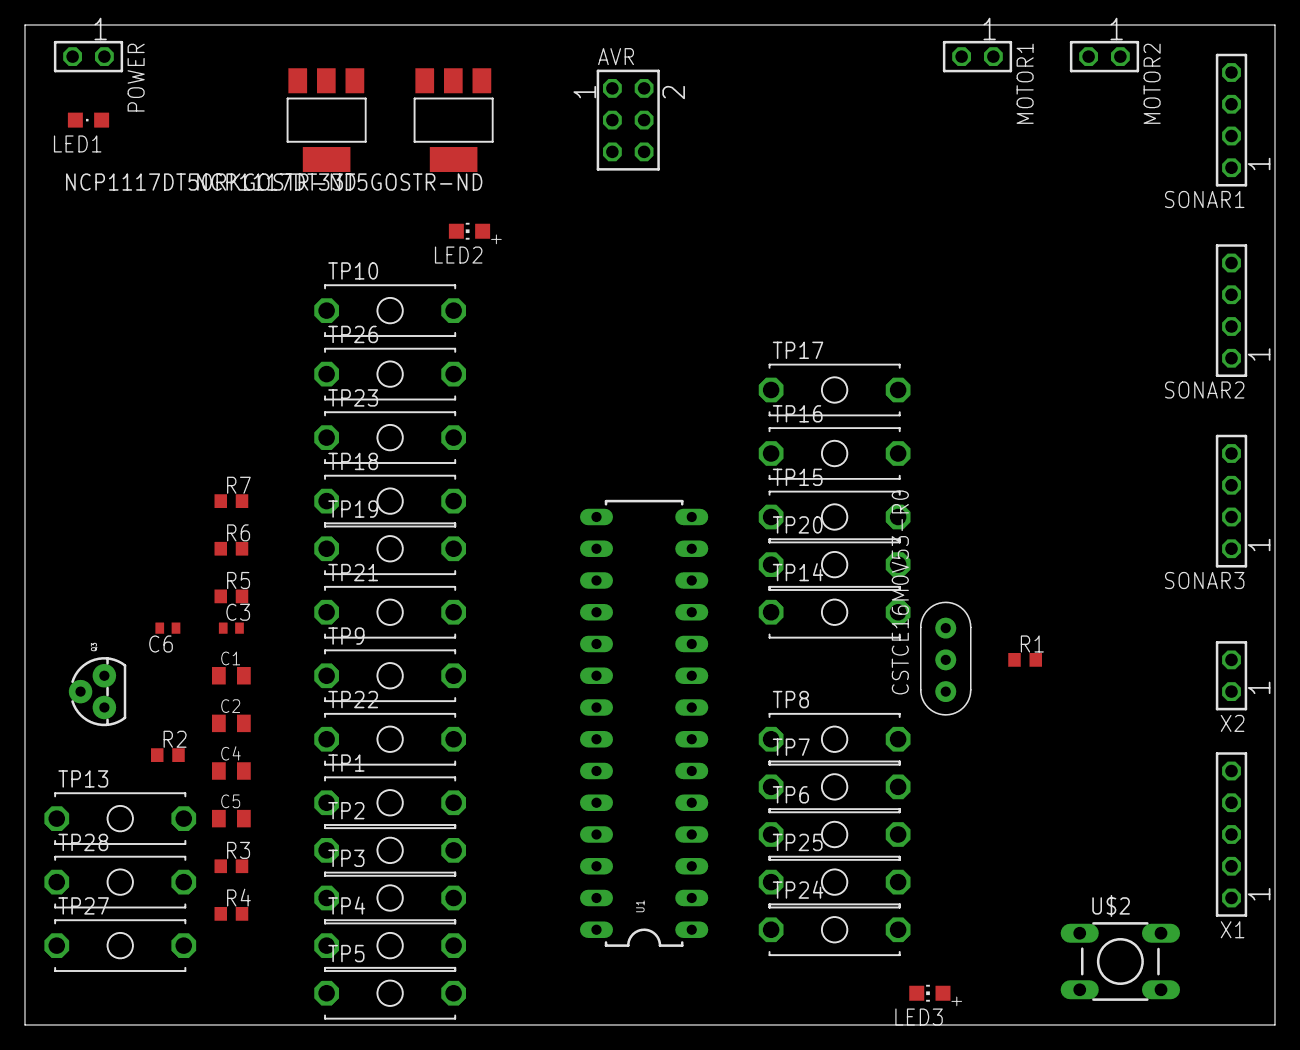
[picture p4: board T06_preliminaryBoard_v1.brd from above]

Board: 2 copper layers, 100.0 x 80.0 mm, 57 parts (0 on the bottom side), 33 nets, no tracks yet.

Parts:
AVR: SSW-103-02-S-D
C1, C2, C4, C5: 10u; C0805K
C3, C6: 100n; C1005
CSTCE16M0V53-R0: 16M; CERM_OSC
LED1: LTST-C171GKT; CHIPLED_0805
LED2: LTST-C171GKT; CHIP-LED0805
LED3: LTST-C170KFKT; CHIP-LED0805
MOTOR1, MOTOR2: SSW-102-02-S-S
NCP1117DT33T5GOSTR-ND, NCP1117DT50RKGOSTR-ND: REG1117; SOT223
POWER: SSW-102-02-S-S
Q3: 2n3904; TO-92
R1: 1M; R0603
R2: 10K; R0603
R3, R6, R7: 220; R0603
R4: 500; R0603
R5: 100; R0603
SONAR1, SONAR2, SONAR3: SSW-104-02-S-S
TP1, TP2, TP3, TP4, TP5, TP6, TP7, TP8, TP9, TP10, TP13, TP14, TP15, TP16, TP17, TP18, TP19, TP20, TP21, TP22, TP23, TP24, TP25, TP26, TP27, TP28: MPB1
U1: ATMEGA328P_PDIP; DIL28-3
U$2: TACTILE-SWITCH-PTH; TAC-SWITCH-PTH
X1: SSW-105-02-S-S
X2: SSW-102-02-S-S

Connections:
+3V3: C4.1, NCP1117DT33T5GOSTR-ND.2, R5.2, TP10.1, TP10.1@1
+5V: AVR.1, C1.1, C3.1, C6.1, NCP1117DT50RKGOSTR-ND.2, R2.2, R3.1, SONAR1.4, SONAR2.4, SONAR3.4, TP9.1, TP9.1@1, U1.7, U1.20, X2.2
+9V: C2.1, C5.1, NCP1117DT33T5GOSTR-ND.3, NCP1117DT50RKGOSTR-ND.3, POWER.1, R6.1, TP26.1, TP26.1@1
BU0: TP25.1, TP25.1@1, U1.2, X1.1
BU1: TP24.1, TP24.1@1, U1.3, X1.2
BU2: TP6.1, TP6.1@1, U1.4, X1.3
BU3: TP7.1, TP7.1@1, U1.5, X1.4
BU4: TP8.1, TP8.1@1, U1.6, X1.5
D16: TP19.1, TP19.1@1, U1.16
ECHO1: SONAR1.2, TP14.1, TP14.1@1, U1.11
ECHO2: SONAR2.2, TP15.1, TP15.1@1, U1.12
ECHO3: SONAR3.2, TP16.1, TP16.1@1, U1.13
GND: AVR.5, C1.2, C2.2, C3.2, C4.2, C5.2, C6.2, CSTCE16M0V53-R0.P$2, LED1.C, LED2.C, LED3.C, NCP1117DT33T5GOSTR-ND.1, NCP1117DT50RKGOSTR-ND.1, POWER.2, Q3.1, SONAR1.1, SONAR2.1, SONAR3.1, U1.8, U1.22, U$2.1, X2.1
MISO: AVR.6, TP21.1, TP21.1@1, U1.18
MOSI: AVR.3, TP20.1, TP20.1@1, U1.17
MOTOR: R4.1, TP17.1, TP17.1@1, U1.14
unnamed: CSTCE16M0V53-R0.P$3, R1.1, U1.10
unnamed: CSTCE16M0V53-R0.P$1, R1.2, U1.9
unnamed: TP23.1, TP23.1@1, U1.23
unnamed: TP1.1, TP1.1@1, U1.24
unnamed: MOTOR1.1, MOTOR2.1, R5.1
unnamed: TP2.1, TP2.1@1, U1.25
unnamed: LED1.A, R6.2
unnamed: LED2.A, R3.2
unnamed: LED3.A, R7.2
unnamed: Q3.2, R4.2
unnamed: MOTOR1.2, MOTOR2.2, Q3.3, TP13.1, TP13.1@1
unnamed: TP3.1, TP3.1@1, U1.26
unnamed: TP4.1, TP4.1@1, U1.27
unnamed: TP5.1, TP5.1@1, U1.28
RESET: AVR.2, R2.1, R7.1, TP27.1, TP27.1@1, TP28.1, TP28.1@1, U1.1, U$2.3
SCK: AVR.4, TP22.1, TP22.1@1, U1.19
TRIG: SONAR1.3, SONAR2.3, SONAR3.3, TP18.1, TP18.1@1, U1.15

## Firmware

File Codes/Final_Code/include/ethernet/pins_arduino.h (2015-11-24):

/*
  pins_arduino.h - Pin definition functions for Arduino
  Part of Arduino - http://www.arduino.cc/

  Copyright (c) 2007 David A. Mellis

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
  $Id: wiring.h 249 2007-02-03 16:52:51Z mellis $
*/

#ifndef Pins_Arduino_h
#define Pins_Arduino_h

#include <avr/pgmspace.h>

#define NUM_DIGITAL_PINS            20
#define NUM_ANALOG_INPUTS           6
#define analogInputToDigitalPin(p)  ((p < 6) ? (p) + 14 : -1)

#if defined(__AVR_ATmega8__)
#define digitalPinHasPWM(p)         ((p) == 9 || (p) == 10 || (p) == 11)
#else
#define digitalPinHasPWM(p)         ((p) == 3 || (p) == 5 || (p) == 6 || (p) == 9 || (p) == 10 || (p) == 11)
#endif

static const uint8_t SS   = 10;
static const uint8_t MOSI = 11;
static const uint8_t MISO = 12;
static const uint8_t SCK  = 13;

static const uint8_t SDA = 18;
static const uint8_t SCL = 19;
#define LED_BUILTIN 9

static const uint8_t A0 = 14;
static const uint8_t A1 = 15;
static const uint8_t A2 = 16;
static const uint8_t A3 = 17;
static const uint8_t A4 = 18;
static const uint8_t A5 = 19;
static const uint8_t A6 = 20;
static const uint8_t A7 = 21;

#define digitalPinToPCICR(p)    (((p) >= 0 && (p) <= 21) ? (&PCICR) : ((uint8_t *)0))
#define digitalPinToPCICRbit(p) (((p) <= 7) ? 2 : (((p) <= 13) ? 0 : 1))
#define digitalPinToPCMSK(p)    (((p) <= 7) ? (&PCMSK2) : (((p) <= 13) ? (&PCMSK0) : (((p) <= 21) ? (&PCMSK1) : ((uint8_t *)0))))
#define digitalPinToPCMSKbit(p) (((p) <= 7) ? (p) : (((p) <= 13) ? ((p) - 8) : ((p) - 14)))

#ifdef ARDUINO_MAIN

// On the Arduino board, digital pins are also used
// for the analog output (software PWM).  Analog input
// pins are a separate set.

// ATMEL ATMEGA8 & 168 / ARDUINO
//
//                  +-\/-+
//            PC6  1|    |28  PC5 (AI 5)
//      (D 0) PD0  2|    |27  PC4 (AI 4)
//      (D 1) PD1  3|    |26  PC3 (AI 3)
//      (D 2) PD2  4|    |25  PC2 (AI 2)
// PWM+ (D 3) PD3  5|    |24  PC1 (AI 1)
//      (D 4) PD4  6|    |23  PC0 (AI 0)
//            VCC  7|    |22  GND
//            GND  8|    |21  AREF
//            PB6  9|    |20  AVCC
//            PB7 10|    |19  PB5 (D 13)
// PWM+ (D 5) PD5 11|    |18  PB4 (D 12)
// PWM+ (D 6) PD6 12|    |17  PB3 (D 11) PWM
//      (D 7) PD7 13|    |16  PB2 (D 10) PWM
//      (D 8) PB0 14|    |15  PB1 (D 9) PWM
//                  +----+
//
// (PWM+ indicates the additional PWM pins on the ATmega168.)

// ATMEL ATMEGA1280 / ARDUINO
//
// 0-7 PE0-PE7   works
// 8-13 PB0-PB5  works
// 14-21 PA0-PA7 works 
// 22-29 PH0-PH7 works
// 30-35 PG5-PG0 works
// 36-43 PC7-PC0 works
// 44-51 PJ7-PJ0 works
// 52-59 PL7-PL0 works
// 60-67 PD7-PD0 works
// A0-A7 PF0-PF7
// A8-A15 PK0-PK7


// these arrays map port names (e.g. port B) to the
// appropriate addresses for various functions (e.g. reading
// and writing)
const uint16_t PROGMEM port_to_mode_PGM[] = {
	NOT_A_PORT,
	NOT_A_PORT,
	(uint16_t) &DDRB,
	(uint16_t) &DDRC,
	(uint16_t) &DDRD,
};

const uint16_t PROGMEM port_to_output_PGM[] = {
	NOT_A_PORT,
	NOT_A_PORT,
	(uint16_t) &PORTB,
	(uint16_t) &PORTC,
	(uint16_t) &PORTD,
};

const uint16_t PROGMEM port_to_input_PGM[] = {
	NOT_A_PORT,
	NOT_A_PORT,
	(uint16_t) &PINB,
	(uint16_t) &PINC,
	(uint16_t) &PIND,
};

const uint8_t PROGMEM digital_pin_to_port_PGM[] = {
	PD, /* 0 */
	PD,
	PD,
	PD,
	PD,
	PD,
	PD,
	PD,
	PB, /* 8 */
	PB,
	PB,
	PB,
	PB,
	PB,
	PC, /* 14 */
	PC,
	PC,
	PC,
	PC,
	PC,
};

const uint8_t PROGMEM digital_pin_to_bit_mask_PGM[] = {
	_BV(0), /* 0, port D */
	_BV(1),
	_BV(2),
	_BV(3),
	_BV(4),
	_BV(5),
	_BV(6),
	_BV(7),
	_BV(0), /* 8, port B */
	_BV(1),
	_BV(2),
	_BV(3),
	_BV(4),
	_BV(5),
	_BV(0), /* 14, port C */
	_BV(1),
	_BV(2),
	_BV(3),
	_BV(4),
	_BV(5),
};

const uint8_t PROGMEM digital_pin_to_timer_PGM[] = {
	NOT_ON_TIMER, /* 0 - port D */
	NOT_ON_TIMER,
	NOT_ON_TIMER,
	// on the ATmega168, digital pin 3 has hardware pwm
#if defined(__AVR_ATmega8__)
	NOT_ON_TIMER,
#else
	TIMER2B,
#endif
	NOT_ON_TIMER,
	// on the ATmega168, digital pins 5 and 6 have hardware pwm
#if defined(__AVR_ATmega8__)
	NOT_ON_TIMER,
	NOT_ON_TIMER,
#else
	TIMER0B,
	TIMER0A,
#endif
	NOT_ON_TIMER,
	NOT_ON_TIMER, /* 8 - port B */
	TIMER1A,
	TIMER1B,
#if defined(__AVR_ATmega8__)
	TIMER2,
#else
	TIMER2A,
#endif
	NOT_ON_TIMER,
	NOT_ON_TIMER,
	NOT_ON_TIMER,
	NOT_ON_TIMER, /* 14 - port C */
	NOT_ON_TIMER,
	NOT_ON_TIMER,
	NOT_ON_TIMER,
	NOT_ON_TIMER,
};

#endif

// These serial port names are intended to allow libraries and architecture-neutral
// sketches to automatically default to the correct port name for a particular type
// of use.  For example, a GPS module would normally connect to SERIAL_PORT_HARDWARE_OPEN,
// the first hardware serial port whose RX/TX pins are not dedicated to another use.
//
// SERIAL_PORT_MONITOR        Port which normally prints to the Arduino Serial Monitor
//
// SERIAL_PORT_USBVIRTUAL     Port which is USB virtual serial
//
// SERIAL_PORT_LINUXBRIDGE    Port which connects to a Linux system via Bridge library
//
// SERIAL_PORT_HARDWARE       Hardware serial port, physical RX & TX pins.
//
// SERIAL_PORT_HARDWARE_OPEN  Hardware serial ports which are open for use.  Their RX & TX
//                            pins are NOT connected to anything by default.
#define SERIAL_PORT_HARDWARE       Serial
#define SERIAL_PORT_HARDWARE_OPEN  Serial

#endif

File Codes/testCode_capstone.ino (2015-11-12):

int led = 9;
String Total, Space; 

void TriggerRead(int echoPin);
long PulseWidth(int echoPin);
int constantDistance = 30;


void setup() {
  Serial.begin(115200);
  pinMode(led, OUTPUT);
  Space = String(' ');
  Total = String();
  digitalWrite(led, LOW);
}

void loop() {
  Total = PulseWidth(5) + Space + PulseWidth(6) + Space + PulseWidth(7);
  Serial.println(Total);
 
  if (PulseWidth(5) < constantDistance || PulseWidth(6) < constantDistance || PulseWidth(7) < constantDistance) {
    digitalWrite(led, HIGH);
  }
  else {
    digitalWrite(led, LOW);
  }


  delay(100);

}

void TriggerRead(int echoPin) {
  pinMode(echoPin, OUTPUT);
  digitalWrite(echoPin, LOW);  // Added this line
  delayMicroseconds(5); // Added this line
  digitalWrite(echoPin, HIGH);
  delayMicroseconds(20); // Added this line
  digitalWrite(echoPin, LOW);
}

long PulseWidth(int echoPin) {
  long duration, distance;
  TriggerRead(echoPin);
  pinMode(echoPin, INPUT);
  duration = pulseIn(echoPin, HIGH);
  distance = (duration / 2) / 29.1;
  return distance;
}

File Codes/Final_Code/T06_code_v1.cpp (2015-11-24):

// Version 1 Code to run on the T06 Board
// Shadman Samin, Nathan Pham, Keon Yoo, Dusan Micic
// The code runs an arduino header files which includes all the basic Arduino Libraries to run the commands.

#include <Arduino.h>

void setup(); // Setup to initialize all the Pins
void loop(); // Main function to run the while loop statement
int led = 9;

void TriggerRead(int echoPin); // This parts sends 10 us Triggers into the HC-SR04
long PulseWidth(int echoPin); // Waits for an interrupt signal and counts the length of the interrupt
int constantDistance = 30; // constant distance that can be changed


void setup() {
  pinMode(led, OUTPUT);
  digitalWrite(led, LOW);
}

void loop() {
  if (PulseWidth(8) < constantDistance || PulseWidth(10) < constantDistance || PulseWidth(11) < constantDistance) {
    digitalWrite(led, HIGH);
  }
  else {
    digitalWrite(led, LOW);
  }
  delay(100); // Gives the Sensor enough time so that trigger does not overlap with the Echo signal
}

void TriggerRead(int echoPin) {
  pinMode(echoPin, OUTPUT);
  digitalWrite(echoPin, LOW); 
  delayMicroseconds(5); 
  digitalWrite(echoPin, HIGH);
  delayMicroseconds(20); // 10 us++ is sent just for safety that the trigger is long enuf
  digitalWrite(echoPin, LOW);
}

long PulseWidth(int echoPin) {
  long duration, distance;
  TriggerRead(echoPin);
  pinMode(echoPin, INPUT);
  duration = pulseIn(echoPin, HIGH); // Interrupt reads the length of the pulse
  distance = (duration / 2) / 29.1;
  return distance;
}

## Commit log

2015-11-05 Made Changes suggested by Andrew. Made a bus connection for possible future port connections. Also, add AVR Programming Chip to code it in.
    [T06_preliminarySchematic_v3.sch]
2015-11-05 Changed the LED package numbers. Added a Orange LED to the Reset Switch. This goes low when the reset is pressed. Fixed the bypass capacitor problems. Added 100nF bypass capacitor to the VCC and AVCC
    [T06_preliminarySchematic_v3.sch]
2015-11-05 Made a new file for Bill of Materials that needs to be ordered as we go along. NEED to be ordered by next week
    [Bill Of Materials.xlsx]
2015-11-05 First version of the board with no routing. Next stage we need to route the wires.
    [T06_preliminaryBoard_v1.brd]
2015-11-05 Rough board. Routing still needs to be done
    [T06_preliminaryBoard_v1.brd]
2015-11-06 Dummy change in Bill
    [Bill Of Materials.xlsx]
2015-11-06 Schematic Revision
    [T06_preliminarySchematic_v4.brd, T06_preliminarySchematic_v4.sch]
2015-11-06 Revert "Schematic Revision"
    This reverts commit 48704319808d7b4bc4e80a9d6127979d2afba1c1.
    [T06_preliminarySchematic_v4.brd, T06_preliminarySchematic_v4.sch]
2015-11-08 made changes to the schematic. Used a different package for the test points as through hole one pin P1-13. Reflected in the schematic. Dusan needs to change and reflect in on the board
    [T06_preliminarySchematic_v3.brd, T06_preliminarySchematic_v3.sch]
2015-11-08 making sure I can do git right before I start changing stuff
    [T06_preliminarySchematic_v3.brd]
2015-11-08 still trying to figutr out git
    [T06_preliminarySchematic_v3.brd, T06_preliminarySchematic_v3.sch]
2015-11-08 practice makes perfect
    [T06_preliminarySchematic_v3.brd, T06_preliminarySchematic_v3.sch]
2015-11-08 board done and routed, managed to do with only 1 via and no air wires
    [T06_preliminarySchematic_v3.brd]
2015-11-09 final design with no drc errors finished
    [T06_preliminarySchematic_v3.brd]
2015-11-09 Changes reflected in the board. Changes made in the master branch. - Dusan
    [T06_preliminarySchematic_v3.brd, T06_preliminarySchematic_v3.sch]
2015-11-09 Testing Branch
    [Bill Of Materials.xlsx]
2015-11-09 added regulator names
    [T06_preliminarySchematic_v3.brd]
2015-11-09 BOM is done
    [Bill of Materials.v1.xlsx]
2015-11-09 changed 500 ohm to 510 ohm
    [Bill of Materials.v1.xlsx]
2015-11-09 created version 4 of the board, project and schematic
    [T06_preliminarySchematic_v4.brd, T06_preliminarySchematic_v4.sch]
2015-11-10 Andrews suggestions implemented, still unsure what package sizes he wants us to fix
    [T06_preliminarySchematic_v4.brd]
2015-11-11 Added mounting holes
    [T06_preliminarySchematic_v4.brd]
2015-11-11 added ultrasonic sensor datasheet
2015-11-11 board minor changes
    [T06_preliminarySchematic_v4.brd]
2015-11-12 Built the prototype. The sensor doesnt allow us the trigger all the sensors in parallel. So we are using individual pins to trigger the sensors. That is reflected in this revision
    [T06_preliminarySchematic_v4.brd, T06_preliminarySchematic_v4.sch]
2015-11-12 Board and project files are removed from the schematic folder to only host schematic files
    [T06_preliminarySchematic_v3.brd]
2015-11-12 Version 4 schematic added to the schematic folder to reflect those changes
    [T06_preliminarySchematic_v4.sch]
2015-11-12 Arduino Prototype Code Version 1
2015-11-13 Made changes to the cap size from 1005 to 0805
    [T06_preliminarySchematic_v4.brd, T06_preliminarySchematic_v4.sch]
2015-11-13 atempted to fix tnames layer, not sure what he meant, it looks fine to me
    [T06_preliminarySchematic_v4.brd]
2015-11-13 Nade some visual changes to TNAMES on the board so that they are not overlapping. Added pin Names to AVR ISP
    [T06_preliminarySchematic_v4.brd, T06_preliminarySchematic_v4.sch]
2015-11-13 minor adjustments
    [T06_preliminarySchematic_v4.brd]
2015-11-13 Components for board ordered. Quantity and price and status reflected on the Bill of Materials
    [Bill of Materials.v1.xlsx]
2015-11-16 Made changes to the bill of materials. Updated the status of shipment
    [Bill of Materials.v1.xlsx]
2015-11-16 Updated the BOM with current shipment status and board order
    [Bill of Materials.v1.xlsx]
2015-11-20 Made changes to the BOM based on current shipment status
    [Bill of Materials.v1.xlsx]
2015-11-24 Final Code Version Uploaded - Using Arduino CPP library and arduino Header files
2015-11-25 Test plan for the final prototype
2015-12-11 board dimension meausre

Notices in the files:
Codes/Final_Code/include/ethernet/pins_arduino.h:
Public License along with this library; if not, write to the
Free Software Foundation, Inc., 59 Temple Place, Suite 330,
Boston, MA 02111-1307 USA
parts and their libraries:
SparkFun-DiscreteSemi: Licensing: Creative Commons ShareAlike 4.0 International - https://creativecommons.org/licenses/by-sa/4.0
